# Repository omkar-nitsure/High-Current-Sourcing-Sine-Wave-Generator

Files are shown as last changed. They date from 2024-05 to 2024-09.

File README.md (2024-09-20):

# High Current Sourcing Sine Wave Generator

Group Members -

1. Omkar Nitsure - 210070057
2. Ojas Karanjkar - 210070040
3. Kushal Gajbe - 210070048
4. Vaibhav Garg - 21d070085 <br>
Github Link - [All files and code Contents](https://github.com/omkar-nitsure/High_Current_Sourcing_Sine_Wave_Generator)

## Introduction

Magnetic Materials are used in many application and in many different equipment for their special properties. But before using them, we need to have in-depth knowledge of their characteristics. This requires performing BH characterization. In BH characterization, we need to apply a sinusoidal voltage of varying amplitude and frequency across the magnetic material and check for the current it draws. Then the current and voltage information can be used to compute the value of B and H. The area enclosed by this curve is an indication of the amount of power dissipation in the material. This and other information is vital for choosing the right material for a specific application.

So, now we understand why BH characterization is important. We need a source which is able to generate a sinusoidal voltage with varying amplitude and frequency and source the current drawn by the magnetic material. The aim of our project is to design such a source.

This problem can be tackled either using a digital + analog or only analog approach. We tried both approaches. We designed an analog only circuit comprising of Class-AB amplifier and for the digital + analog we have used a Class-D amplifier based circuit. Let's discuss both the approaches in the following sections -

## Target Specifications

We were required to build a source satisfying the above constraints -

- Output Frequency = 2-3 kHz
- Output Sine amplitude = upto 30 Vpp
- Current Sourcing capacity = 1-1.5 A
- Added functionality of allowing user to change frequency on the go using a knob. - Display the current frequency on a LCD screen for ready reference

## Class Ab Based Circuit

In this approach, we designed a circuit which can be broken down in a Voltage amplification circuit and a Current sourcing circuit and connected them in cascade. The circuit diagram is as follows -

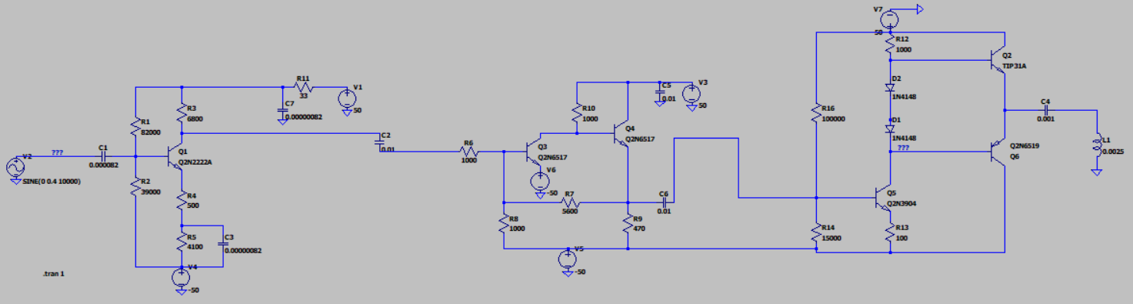
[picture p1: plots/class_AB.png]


Figure 1: Circuit diagram for Class AB amplifier based circuit
The above circuit was giving the correct required output but there was an issue. There was a lot of power dissipation in the different BJTs which would have required big heat sinks and also a lot of power would have got wasted along with the unavoidable power loss due to eddy currents. We tried changing a lot of different parameters but we were not able to reduce the power-loss to the desired levels. While we were searching for the potential solution, we came across class-D amplifier which was not having the issue of power loss. After a lot of brainstorming, we decided to scrap this approach and continue with the approach involving Class-D amplifier.

## Class D Amplifier

Class D amplifier consists of a full-bridge MOSFET based circuit. Each of the 4 MOSFETs are fired by 4 different PWM signals across their gate-source. Two MOSFETs in the same leg get complementary PWM signal such that there ON times are separated by a non-zero dead time.

This dead-time is provided to ensure that there is sufficient time for the MOSFETs to change their states ensuring that both MOSFETs don't turn-on together and short Vdd with GND.

The duty ratio of the PWM signals vary sinusoidally which enables the output to be sinusoidal.

Duty ratios of the 4 PWM signals are as follows -

$$
d_{1} = \frac{1}{2} + m \sin(\omega t)
$$

$$
d_{2} = \frac{1}{2} - m \sin(\omega t)
$$

Then d3 and d4 are just complements of d1, d2 respectively seperated by dead time.

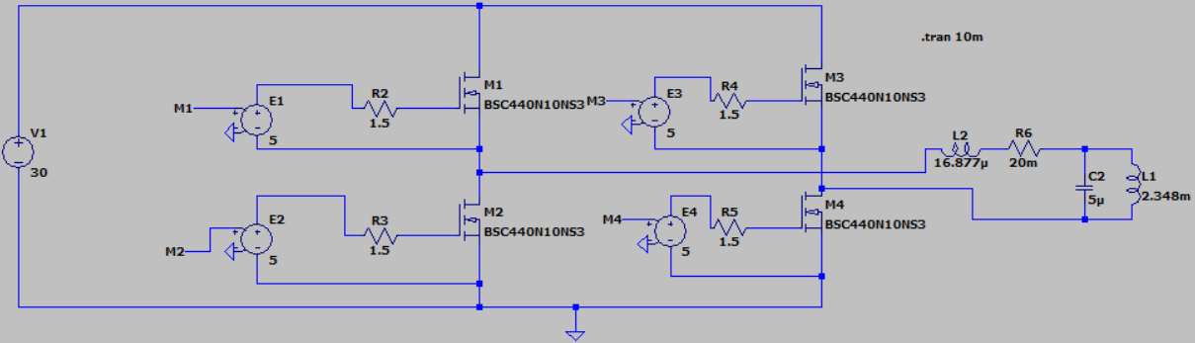
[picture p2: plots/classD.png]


Figure 2: full-bridge MOSFET based circuit

## A. Simulations

We performed the LTSpice simulations of class D amplifier for our required specifications and got desired results. We generated the sinusoidally varying PWM signals by giving a triangular wave and a sine wave as inputs to a comparator. We kept zero dead time assuming perfect switching of MOSFETs. The MOSFETs were switching at a frequency of 100kHz and we tested the sinusoidal outputs for frequencies till 3kHz which was our target specification. We also checked for the power dissipation in the entire circuit(in all components) and found that they were in mW. Thus this approach allowed us to generate sine waves of large amplitudes for frequencies upto 3kHz without requiring any heat-sink at all!! This approach has some cons but that is a trade-off for excellent efficiency. The main limitation of this approach is that it generates saw-tooth noise because of MOSFET switching whereas a purely analog approach will not add any such noise. The results of our simulations are given below where the output voltage across the inductive load is given at the edge of our required specifications. We also give the corresponding current drawn by the inductive load which is well within our specifications.

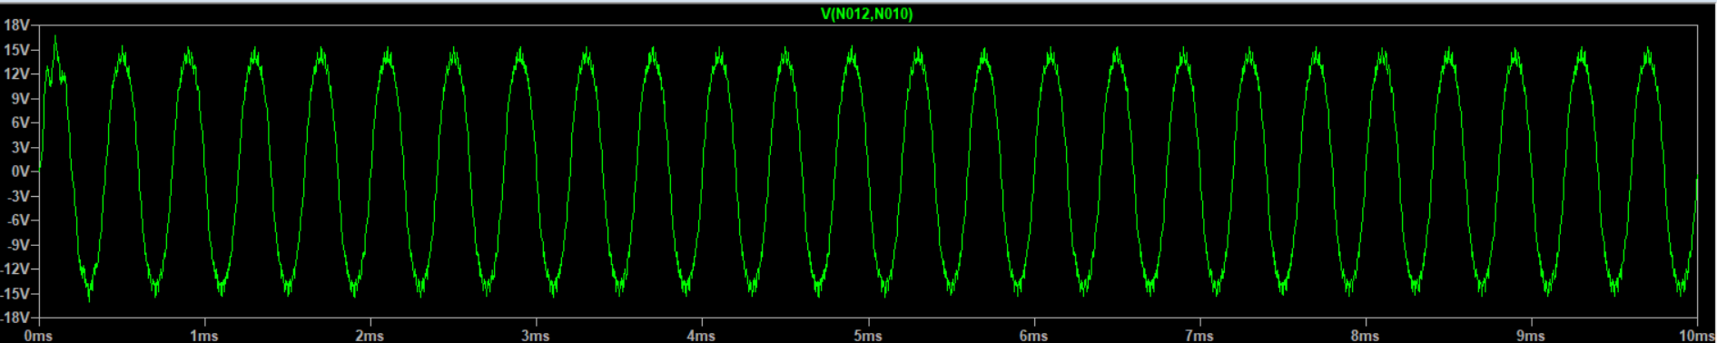
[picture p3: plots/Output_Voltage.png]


Figure 3: output voltage across load

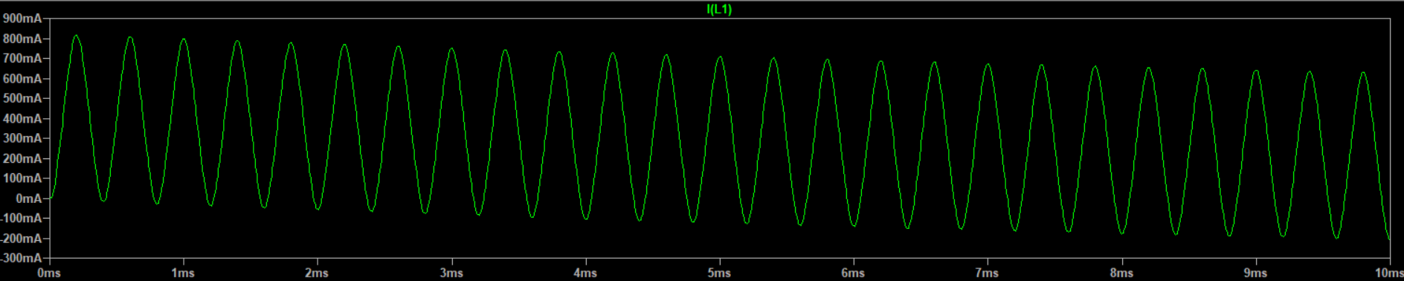
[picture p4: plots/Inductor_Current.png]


Figure 4: Current through the inductive load

## B. Choice Of Bom And Justifications

The Bill of Materials required for our circuit is as follows -

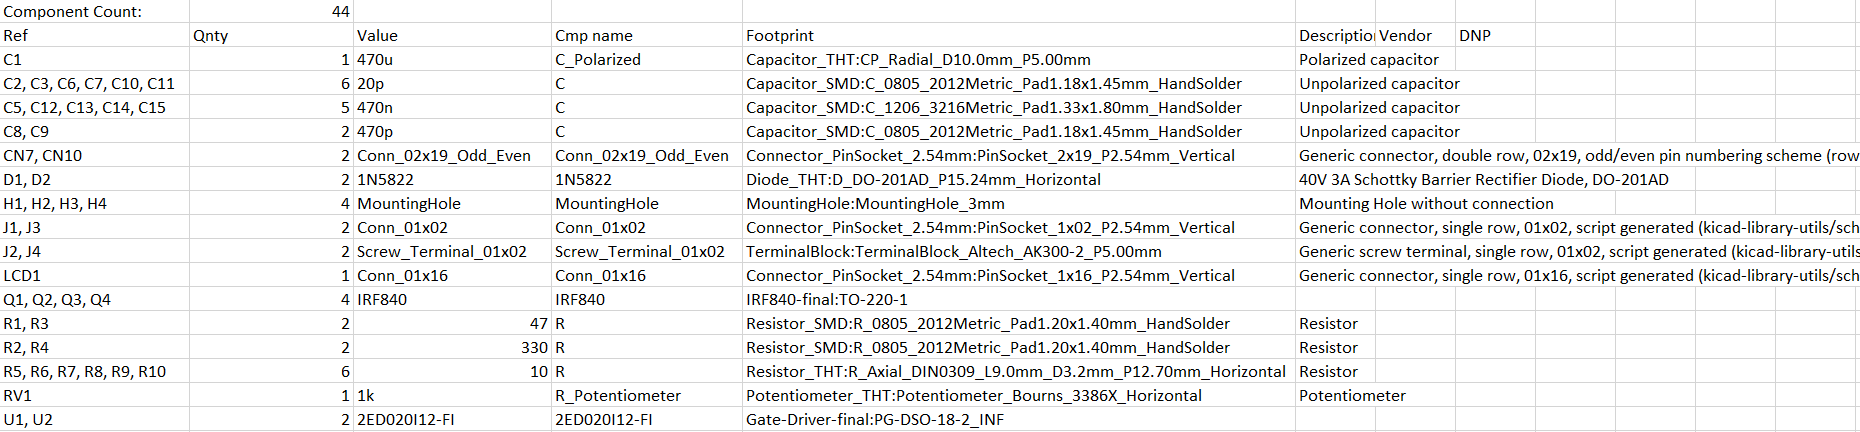
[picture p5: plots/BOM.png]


Figure 5: Bill of Materials

Gate Drivers - The PWM output cannot be directly given to the gates of MOSFETS as the back-currents generated while a MOSFET is turning-OFF will certainly damage the GPIO
pins on the Micro-controller. We wanted to have a gate driver which can amplify the rail-to-rail logic of 3.3 V coming from the micro-controller to rail-to-rail logic of 15V. We also wanted the current sinking capacity to be high which will allow us to switch at much higher frequency. Thus we chose the 2ED02012-FI gate driver from Infenion STM32 minimum package called Bluepill was more than sufficient for our ap-
Bluepill -
plication. It was able to generate the 4 independent PWM signals. It also had ADC which was used to provide the functionality of a knob for changing the output frequency to the user. We also needed 4 additional analog pins to write current frequency value on the LCD display. All of these requirements were satisfied by Bluepill.

RC filter at the input of the gate driver - This low-pass filter was used to remove the high-frequency peaks in the PWM outputs of the microcontroller.

MOSFET - We wanted to produce output sinusoidal signals of 30 Vyp and thus the Vas specifications of the MOSFETs must be larger than this value. We also wanted to source currents upto even 2A and thus the Ids rating must be larger than this value. We also wanted the MOSFET
to be a power MOSFET having the capability of very fast switching. MOSFET named IRF840 satidfied all these constraints and thus we chose that MOSFET for the circuit. LC circuit at the output - We had to use a low-pass filter at the output of a Class-D
amplifier to remove the saw-tooth noise added due to switching. We could have used a RC
filter but that would have resulted in large power-loss in the resistor, so we chose to use LC
filter of appropriate value which would not cause any power-loss.

## Microcontroller Programming

We generate the PWM signal with Sinusoidally varying dead time using the STM32 Bluepill microcontroller. The microcontroller clock frequency is 8MHz. The internal circuitry increases it such that the timers(which we used) get a frequency of 64MHz while the ADC sampling frequency is 8MHz. We decided to keep the switching frequency to be 100kHz which is almost 33 times larger than the maximum rated frequency of our system. It is also well within the maximum attainable switching frequency by the Power MOSFET. We have kept the cut-off frequency to be 12kHz which is less than 10 times the maximum rating. Let us now see how did we generate the PWM signal with sinusoidally varying duty ratio.

## A. Pwm Generation

We used 2 channels from TIM1 on the STM32. Each of these channels have a register named CCR which can be used to manipulate the duty ratio of the microcontroller. So, we stored the values for 1 cycle of the sinusoidal signals corresponding to d1 and d2 in the memory and read those values after a frequency dependent delay. This allowed us to generate sinusoidally varying PWM. Dead-time was also provided to ensure proper switching without any shorting which might damage the MOSFETs. We used a constant dead time of 0.125 us

## B. Adc Interfacing

We wanted to give a simple knob-based control to the user which he can use to set the output frequency he wants. This knob was made using a potentiometer circuit where the ends of the potentiometer are connected to the GND and 3.3V of the microcontroller. The middle pin is connected to the ADC and the values of voltage read using the ADC are then mapped to appropriate frequencies. The ADC is sampled every 1000 cycles to ensure that we don't sample "too often".

## C. Lcd Interfacing

We have also interfaced the LCD with the system so that user can see the current frequency output from the system in real time and adjust the knob accordingly to set the frequency of his choice. We implement the interfacing with 6 pins, 4 of which are the actual data pins. We write the frequency value after every 1000 cycles right after sampling the ADC. Thus we ensure that we don't write to the LCD "too often". The CAD model was then made accordingly to ensure that the LCD is clearly visible to the user.

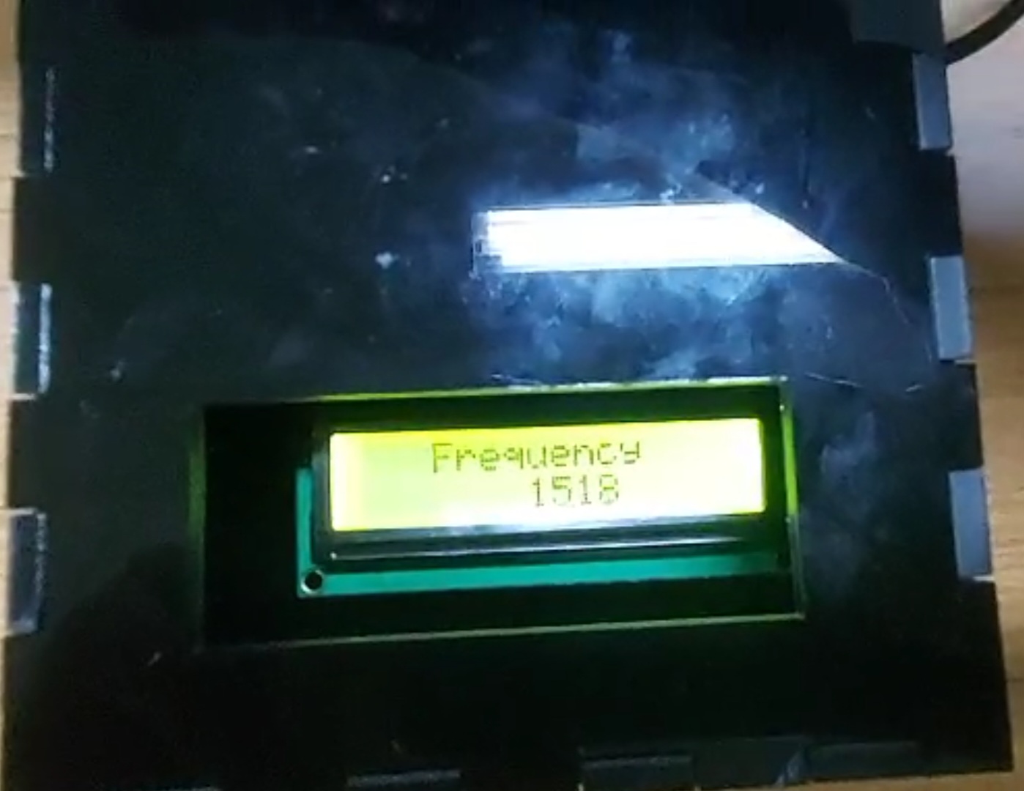
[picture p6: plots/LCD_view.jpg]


Figure 6: LCD in the final prototype

## D. Microcontroller Pinout

The final microcontroller pinout after setting all the GPIO pins and interfacing the ADC and LCD is as follows -
s_JTCK-SW

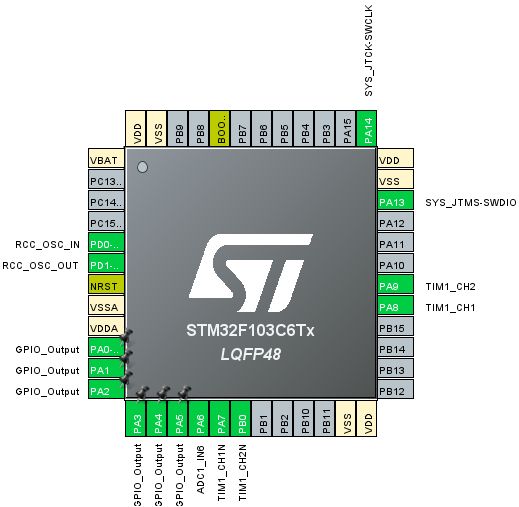
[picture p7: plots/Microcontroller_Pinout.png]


Figure 7: STM32 pinout

## Schematics

Having selected the class D amplifier as the base of our power amplifier, we started making the overall complete circuitry for our prototype. As we have seen so far, our circuit majorly consists of 3 parts, viz

1. Microcontroller - For generating PWM signals.
2. Gate Drivers - For interfacing microcontroller with MOSFETs.
3. Full-bridge MOSFET
In our circuit, we have directly used Blue-Pill, which is a miniature version of NUCLEO-
F103RB STM32 evaluation board. The reason for going with blue-pill is simply because it contains all of the features of NUCLEO board we required and moreover, it is smaller in size.

However, one main issue while using blue-pill is that it does not have emulator part, which is present in NUCLEO board, making it difficult to dump code onto it. We had to use the ST-Link debugger everytime we wanted to dump our code onto blue-pill.

Moving onto the next part of our circuit, we have Gate Drivers. We chose the 2ED020I12-FI
IC manufactured by Infineon. The IC can sustain high voltage up to 1.2kV, supplying currents up to 1A or -2A. The PWM signals generated by the blue-pill were then fed to the gate drivers through the RC filter. This reduces the spike levels due to switching in the microcontroller.

A major part of the gate driver circuitry is the Bootstrap circuit at the high-side output of the gate driver IC. The bootstrap circuitry is used to supply bias to high-side FET. When the low-side FET is ON, the HS pin and source of the high-side FET are pulled to the ground.

As a result, the bootstrap capacitor is charged to Vdd. When the high-side FET is ON in the next cycle, the bootstrap capacitor discharges some of its charge to the gate of FET, thereby creating some positive Vgs and turning on the FET. Schottky diode is used as the bootstrap diode because of its ability to switch at high frequencies. Calculation of bootstrap capacitance is an important step while designing the bootstrap circuit. The value of bootstrap capacitor is calculated according to the given formula -

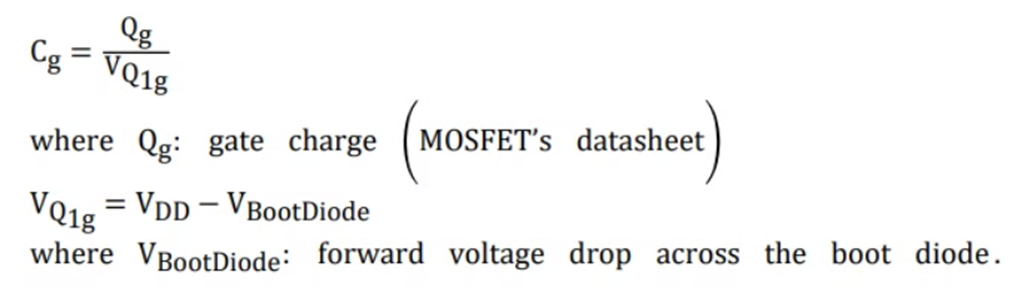
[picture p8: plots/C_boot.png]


Figure 8: Gate Driver Circuit
For IRF540N, the value of gate charge is 66nC, and for 1N5822 Schottky diode, the forward voltage drop is 0.525 V, and Vdd = 15V. Plugging the values in above formula gives, Cg =
4.56 nF The minimum value of bootstrap capacitance should be chosen such that, Cboot =
10xCg Therefore, the value of bootstrap capacitor should be atleast 45nF. Apart from that, we also need to add a bypass capacitor value to Vdd, and the value of bypass capacitor should be atleast 10x the bootstrap capacitance. Therefore, Cbypass should be atleast 450nF.

Now, finally, once we have the pulses at the output of gate drivers, they are passed onto the respective gates of the FETs. The pulses are passed onto the gates of FETs through a resistor.

The output is observed between the source of the two high-side FETs. An electrolytic capacitor is connected between the Vdd and GND and ceramic capacitors need to be connected betweent the drain and ground of each FET. A simple low pass filtering is performed at the output to

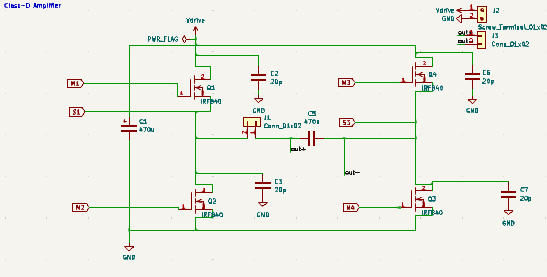
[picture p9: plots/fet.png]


Figure 9: Class-D amplifier
remove spikes due to switching.

We have also added a provision in our circuit to control the frequency using a knob. The knob is connected to a 10kΩ potentiometer. Based on the voltage at the middle terminal of the the voltage is sensed by the ADC in the blue-pill and it is mapped to the corresponding frequency value. The current frequency value is displayed using an LCD. Finally, putting all parts together, we get our final circuit schematics.

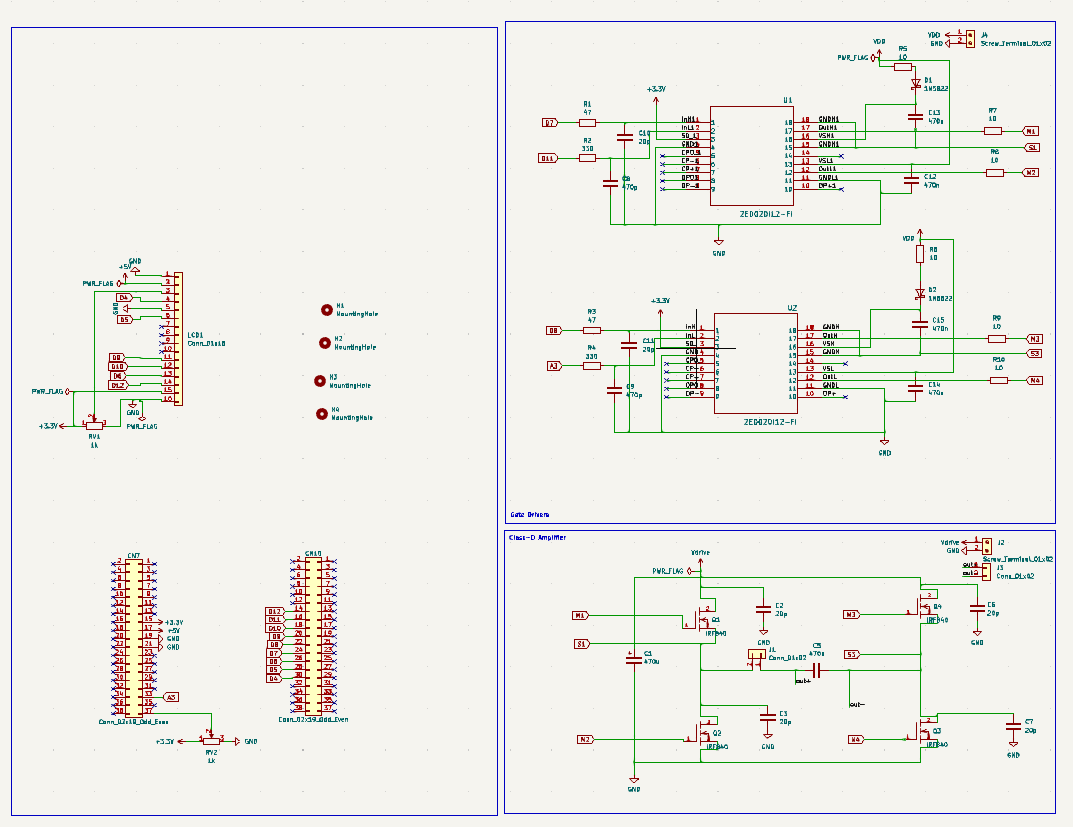
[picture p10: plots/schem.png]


Figure 10: Full circuit schematics

## Intermediate Testing

## A. Pwm Generation

As descibed in 5.1, we generated the PWM signals using STM32 and tested. The output is shown in the image below.
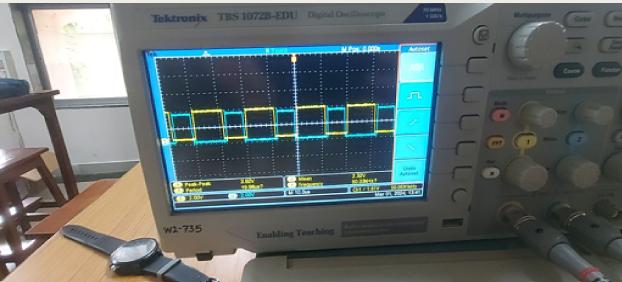
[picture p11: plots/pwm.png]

Figure 11: PWM testing

## B. Adc Interfacing

We were able to interface a potentiometer with the microcontroller using an ADC successfully.

## C. Breadboard Testing

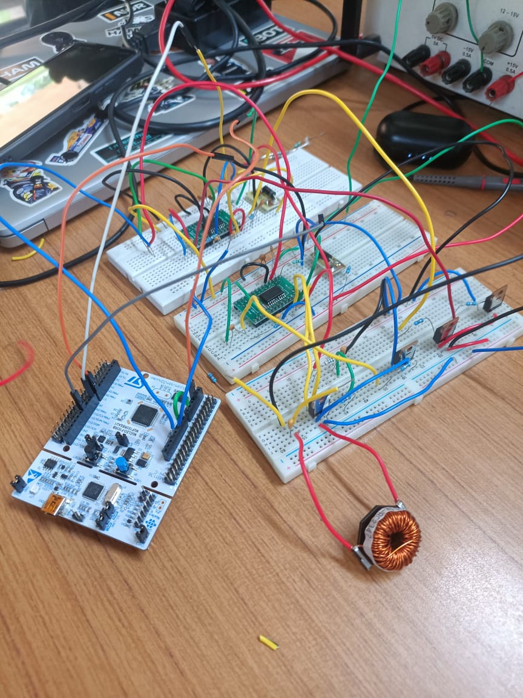
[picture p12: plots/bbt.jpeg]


## Pcb Design

We designed the PCB using the KiCAD software. Various layout rules such as obtuse angles between tracks, decoupling capacitors, and correct placement of components were taken care of. We have used both SMD and THT components in our design. We have majorly used SM
components for decoupling capacitors and the gate driver IC. We have used screw terminals for connecting the inputs to the PCB. The blue pill is mounted on the PCB using a breakout board.

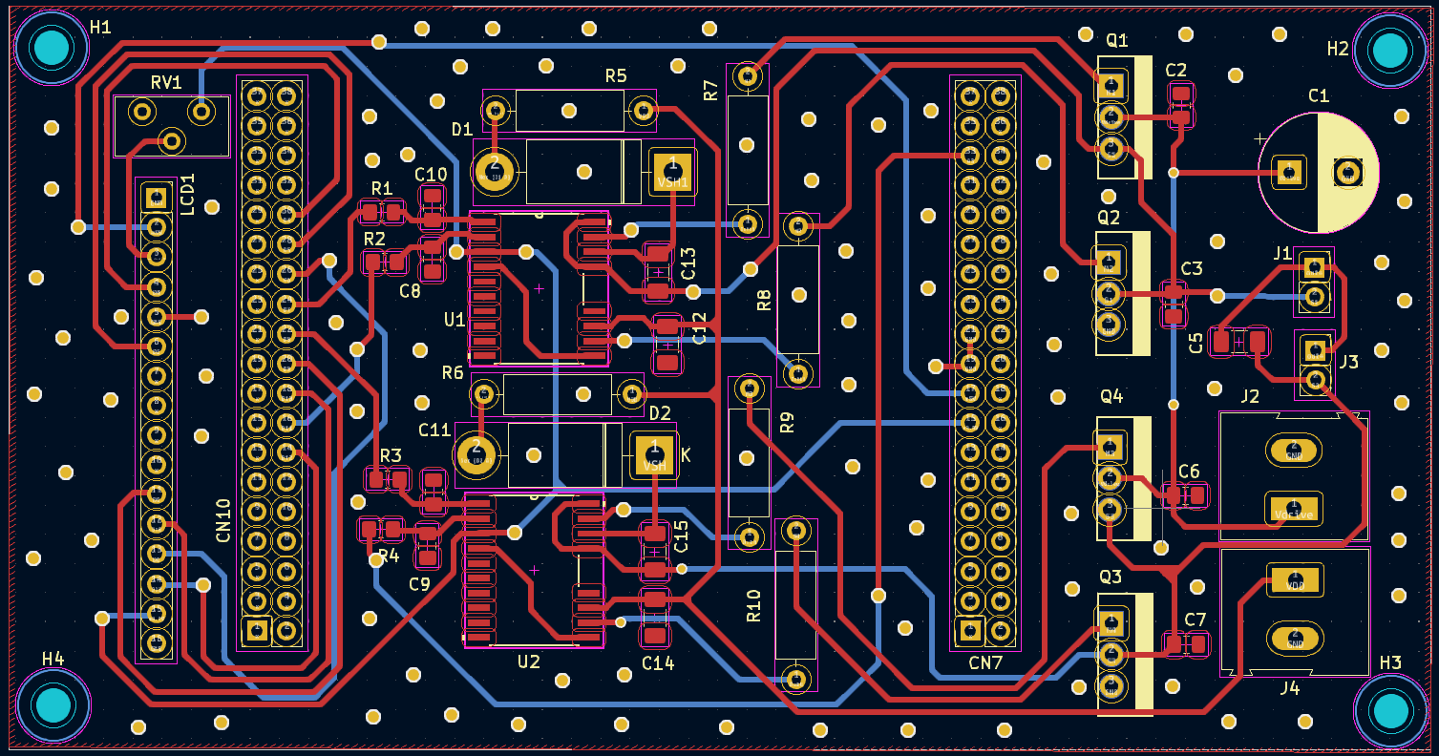
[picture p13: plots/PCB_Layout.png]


Figure 12: PCB Layout

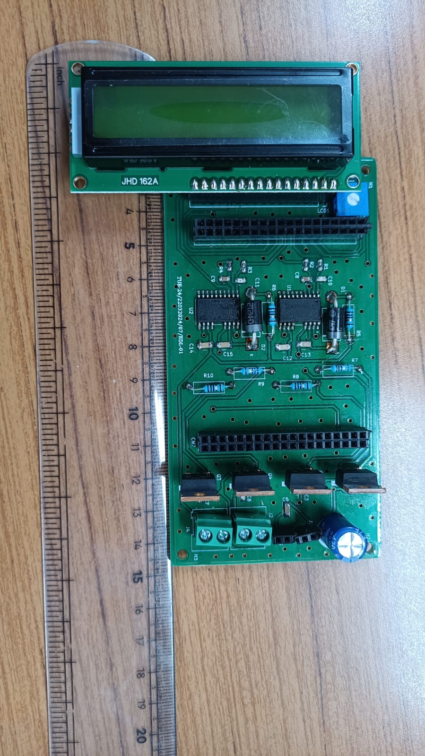
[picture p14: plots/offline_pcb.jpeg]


Figure 13: PCB with all components

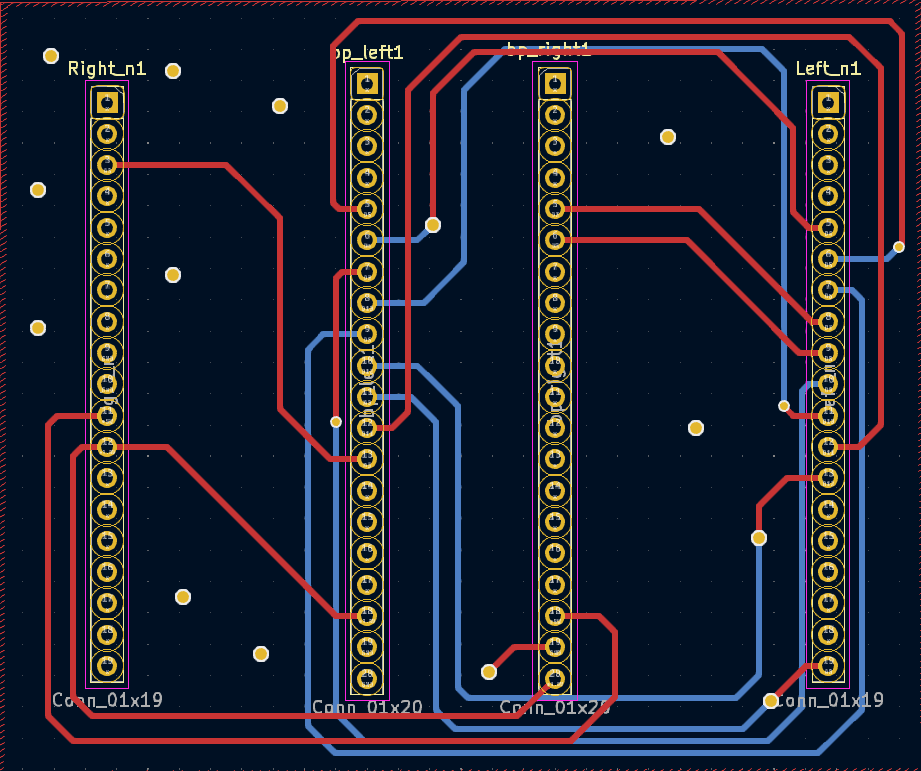
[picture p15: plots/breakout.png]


Figure 14: PCB for breakout board

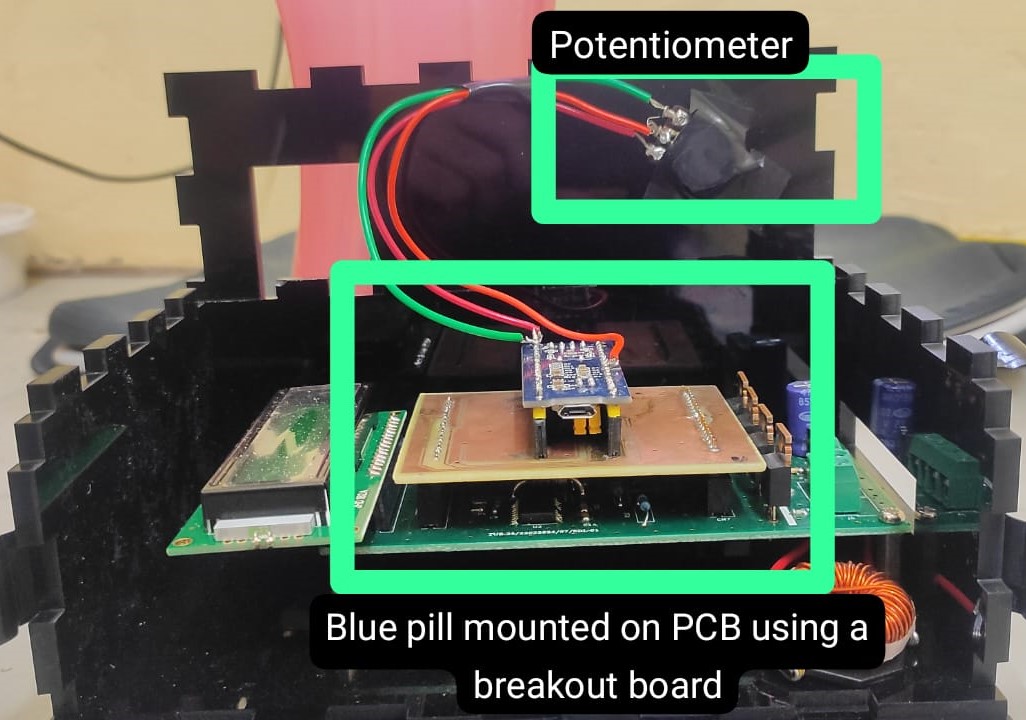
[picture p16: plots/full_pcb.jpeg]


Figure 15: Final PCB

## Cad Design

For our CAD design, we initially planned a 3D box structure using Fusion 360 software. The design process involved careful planning to ensure accessibility to certain components from the outside world while the prototype remains inside the box.

## A. Design Requirements

1. LCD Display: The design incorporates an open area for the LCD display to allow users to observe the frequency without obstruction.

2. Input and Outputs:

- Power Supply: A 5V supply is provided through a USB cable, which is also utilized for burning code onto the STM32 microcontroller.
- External Supplies: Vdrive and Vdd are supplied externally.
- Output Access: The output across the capacitor is also accessible through an opening on the 3D box.
- Potentiometer: A potentiometer is mounted on the box which will be used for controlling the frequency of the prototype. Thus, certain areas must be opened up on the box for the same.

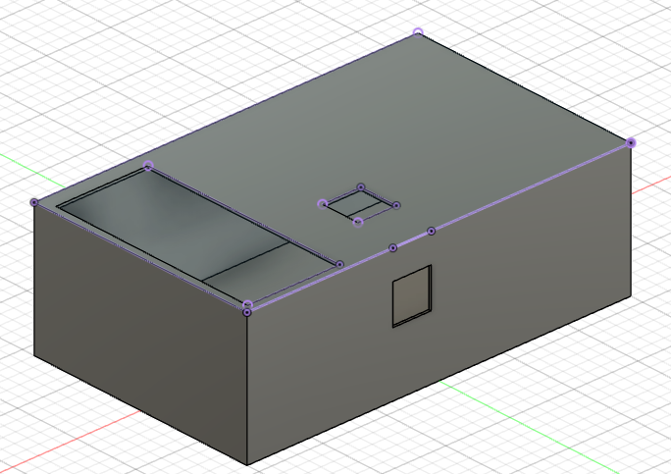
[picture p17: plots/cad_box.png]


Figure 16: 3D box CAD design
However, after discussing the design with the faculty we concluded that 3D printing the box is not possible, and hence we would have to use acrylic sheets laser cutting to make our box.

Now, makercase was used for making the dxf file which has the thickness of the sheet, length, and width for each side of the box. After importing this dxf file into the Fusion 360 software, we cut out the same regions as in the 3D box design.

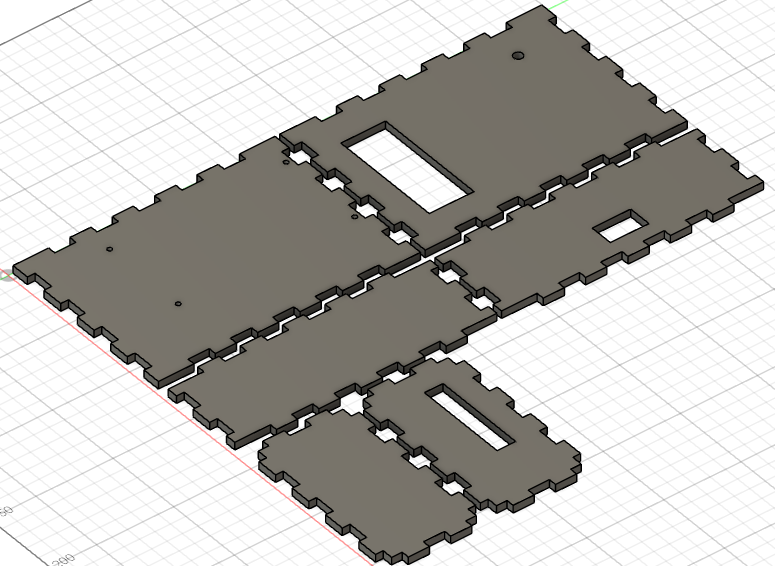
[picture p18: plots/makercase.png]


Figure 17: Acrylic sheets design for the box

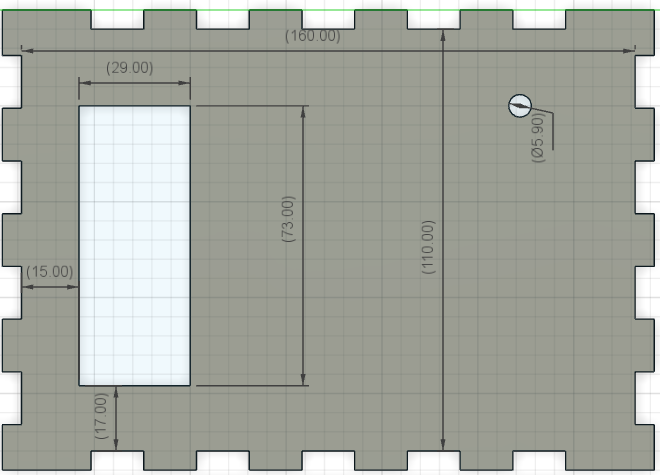
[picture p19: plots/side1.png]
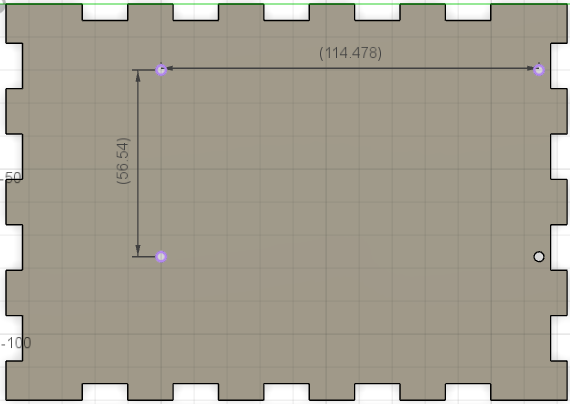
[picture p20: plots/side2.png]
|  |  |
| ----------------------------------- | ----------------------------------- |
| (a) Top side                        | (b) Bottom side                     |

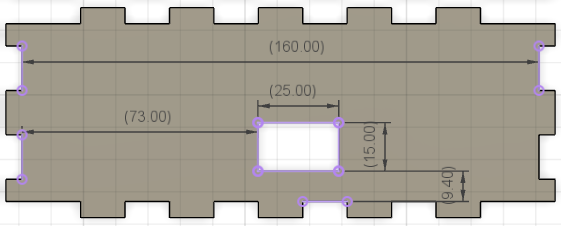
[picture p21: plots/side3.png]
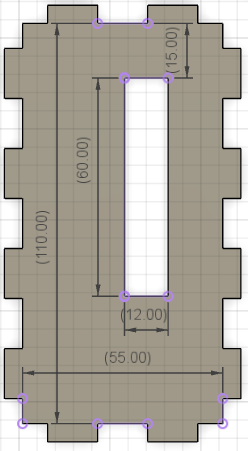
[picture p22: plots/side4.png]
|  |  |
| ----------------------------------- | ----------------------------------- |
| (c) Front view side                 | (d) Side view                       |

Figure 18: Dimensions and open areas in the design.

## Final Prototype

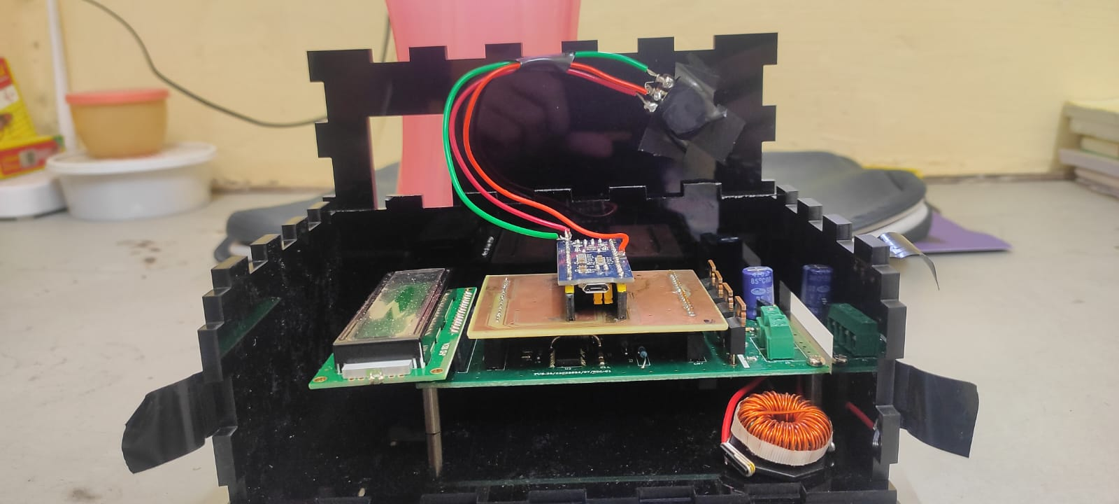
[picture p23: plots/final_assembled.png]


Figure 19: Final Prototype

## Results

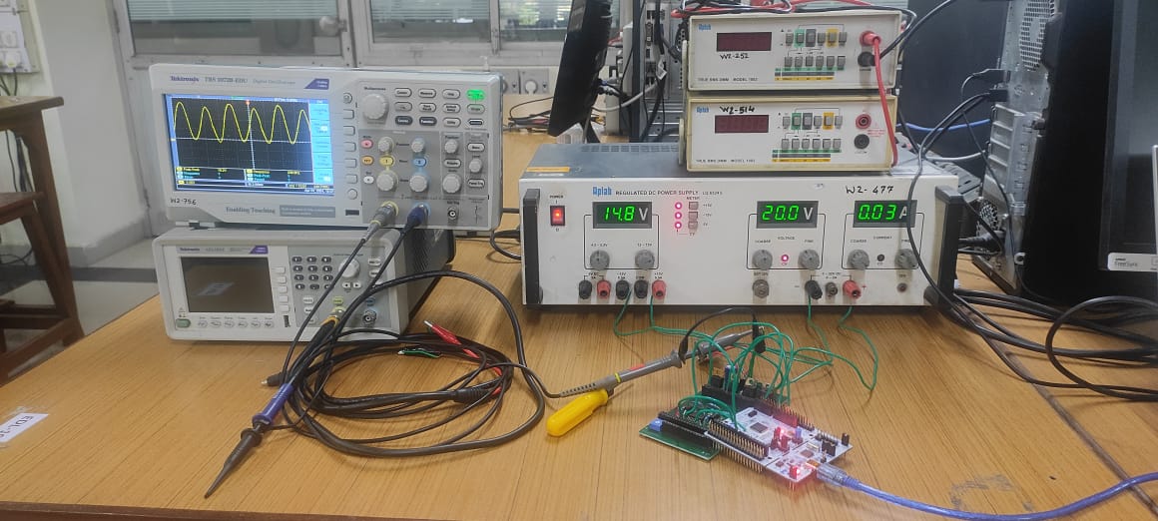
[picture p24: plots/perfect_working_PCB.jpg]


Figure 20: Final output Sine waveform
Our final output waveform is a sine wave meticulously designed for the characterization of magnetic materials. The waveform is derived from three power sources: Vdrive, Vdd, and a 5V supply via USB to the Nucleo board. The output signal is measured across a 470nF capacitor. Our setup achieves a current rating of 1.4 A, with the peak-to-peak voltage (Vpp) reaching up to 30 V at a frequency of 500Hz.

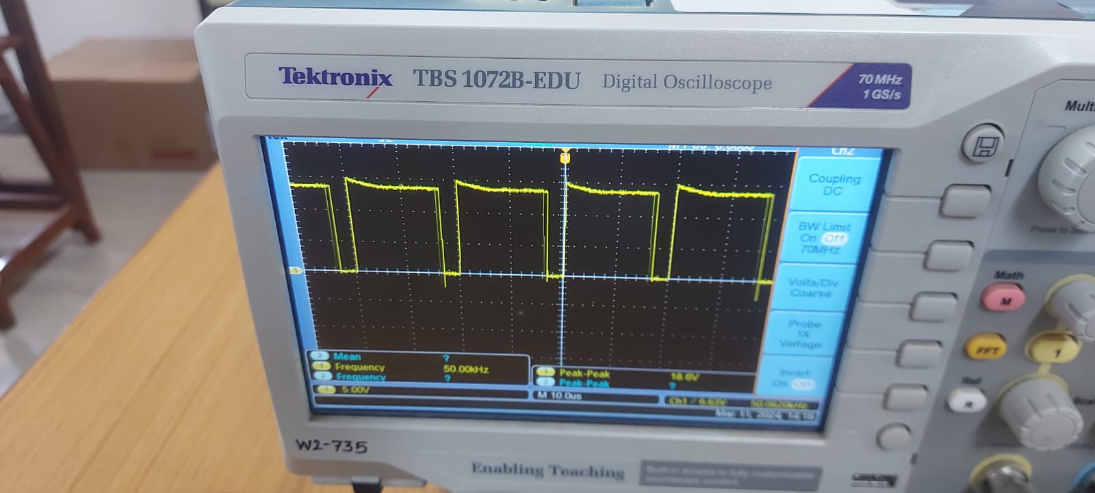
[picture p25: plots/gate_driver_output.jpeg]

Figure 21: Gate Driver output

The output from the gate driver pertains to the high side. As anticipated, it effectively amplifies the PWM signal from the microcontroller. We are able to achieve 18.6 V of peak-topeak voltage output from the gate driver.

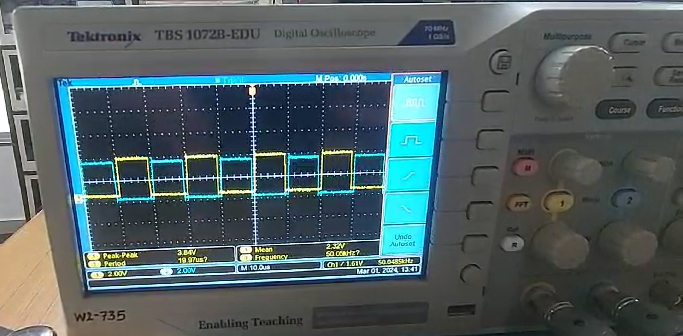
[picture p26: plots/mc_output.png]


Figure 22: Microcontroller output. 
Above is the microcontroller PWM output. This goes as an input to our gate drivers. This PWM peak-to-peak voltage is 3.84 V. This is then amplified to 18.6 V by the gate drivers.

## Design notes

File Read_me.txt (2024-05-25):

                                       READ ME FILE
---------------------------------------------------------------------------------------------
----------------------------------------------------------------------------------------------

1. CAD - Design files for the project used in Autodesk Fusion 360.

2. datasheets:- Datasheet of important components used in our circuit design

3. Images:- All outputs and PCB images of the project

4. LTSpice_Simulations:- LTSpice files for our final circuit. Simulation images are included inside.

5. Papers:- All the research papers which we had referred to for our project. 

6. PCB_Files:- PCB files generated for our circuit design in the KiCAD software. 

7. Report:- Final report of our project. It has everything we have done in our project. 

8. STM32_Bluepill_code:- Main code which was used for making PWM and LCD interfacing. Programming done in CUBEIDE.

9. project_plan.pdf:- It has our decision making and the plan for our project which we had followed. 

10. USER-Manual:- User manual for using the prototype. 

---------------------------------------------------------------------------------------------
---------------------------------------------------------------------------------------------

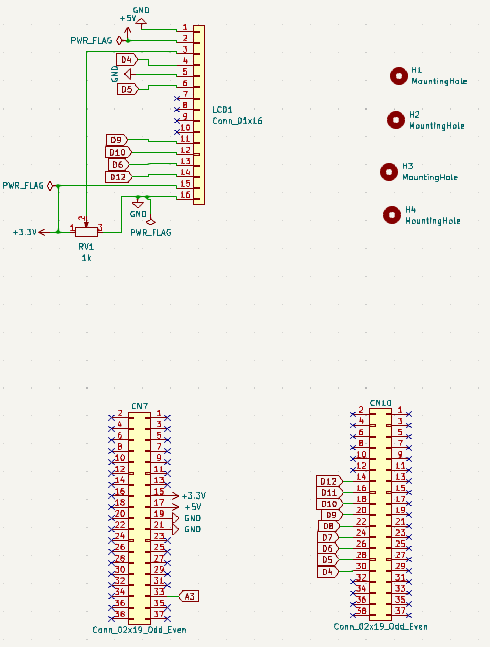
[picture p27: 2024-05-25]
Images/LCD_Microcontroller_Schematic.png

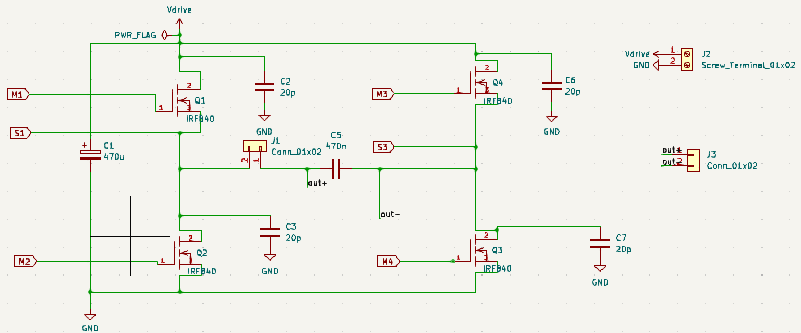
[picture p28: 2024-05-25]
Images/ClassD_Amplifier_Schematic.png

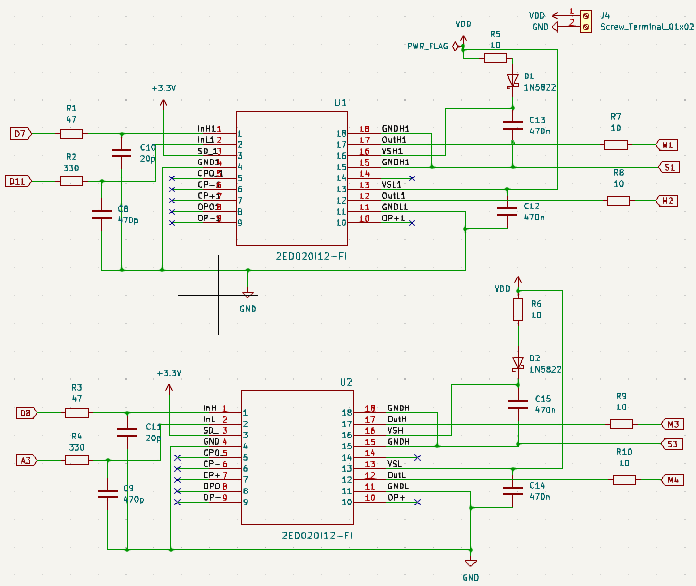
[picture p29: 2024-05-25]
Images/Gate_Driver_Schematic.png

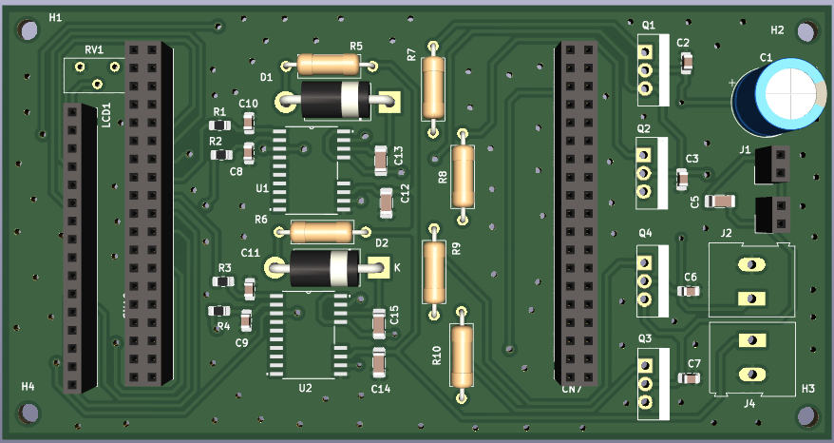
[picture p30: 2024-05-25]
Images/PCB_3DViewer.png

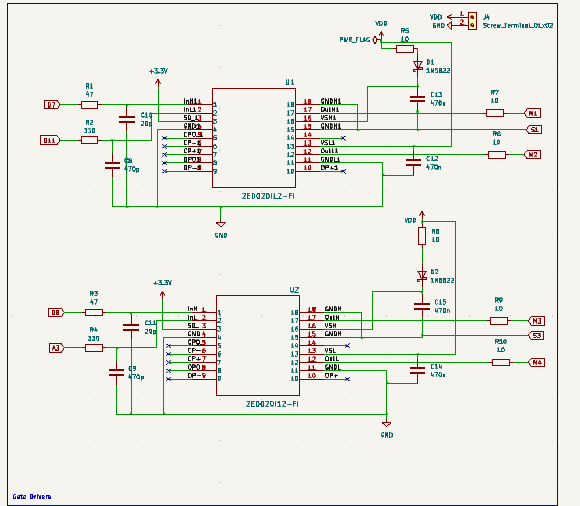
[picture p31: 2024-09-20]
plots/gate_drivers.png

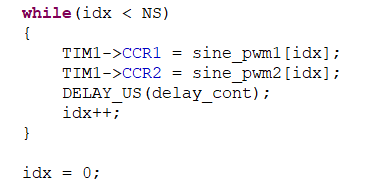
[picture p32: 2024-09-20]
plots/PWM_snippet.png

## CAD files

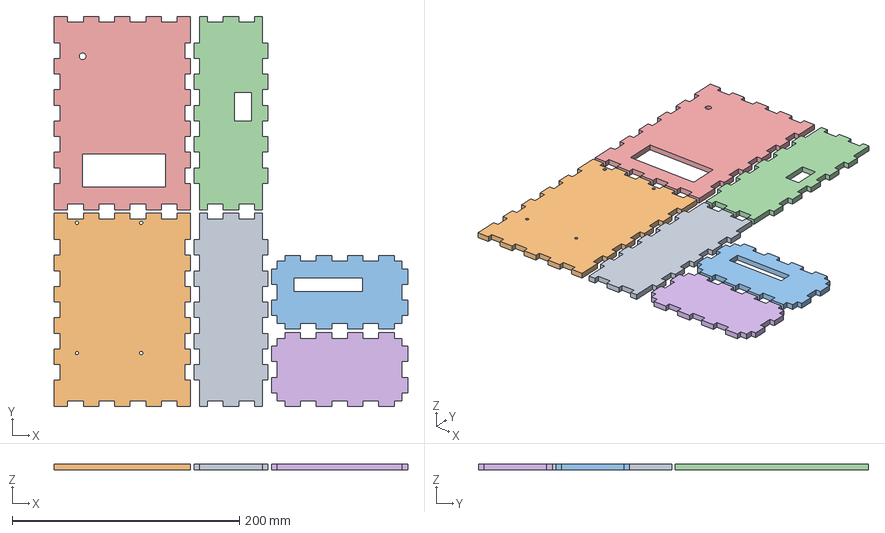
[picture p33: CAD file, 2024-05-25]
CAD/box_box_ii v2.3mf
311.0 x 343.0 x 5.00 mm

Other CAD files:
CAD/box_box_ii v2.dxf
CAD/box_box_ii v2.f3d
CAD/box_box_ii v2.ipt

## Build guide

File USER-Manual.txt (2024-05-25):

                      USER MANUAL         
--------------------------------------------------------------------------

1. There are three inputs to the prototype. 
	i. Vdd :- takes value of 15V 
	ii. Vdrive (or Vin) :- 0-30V
	iii. USB :- gives 5V supply and can also be used for dumping a different code on the Bluepill.

2. There is a rotary knob for potentiometer. This is used to vary the frequency of the final output sinusoidal waveform. 

3. Vpp for output sine wave can be varied by changing Vdrive. 

4. LCD display is used for displaying the output sine wave frequency. It varries by a few Hz from the actual frequency. 

5. Inductor load is connected on external breadboard. Range:- 1 to 10 mH. 

6. Series resistor load with the inductor is also connected on external breadboard. Range:- 0 to 10 ohms. 

7. Frequency display range:- upto 3kHz. 

8. Current across resistive load - for R = 1.2 Ohm and L = 1mH we get current upto 3.16 A

9. Output is taken from female header output pin which is not adjacent to the electrolytic capacitor, i.e leave the pair of pins adjacent to the electrolytic capacitor and take output from the next pair of pins. 

System should be able to drive currents lower than this value

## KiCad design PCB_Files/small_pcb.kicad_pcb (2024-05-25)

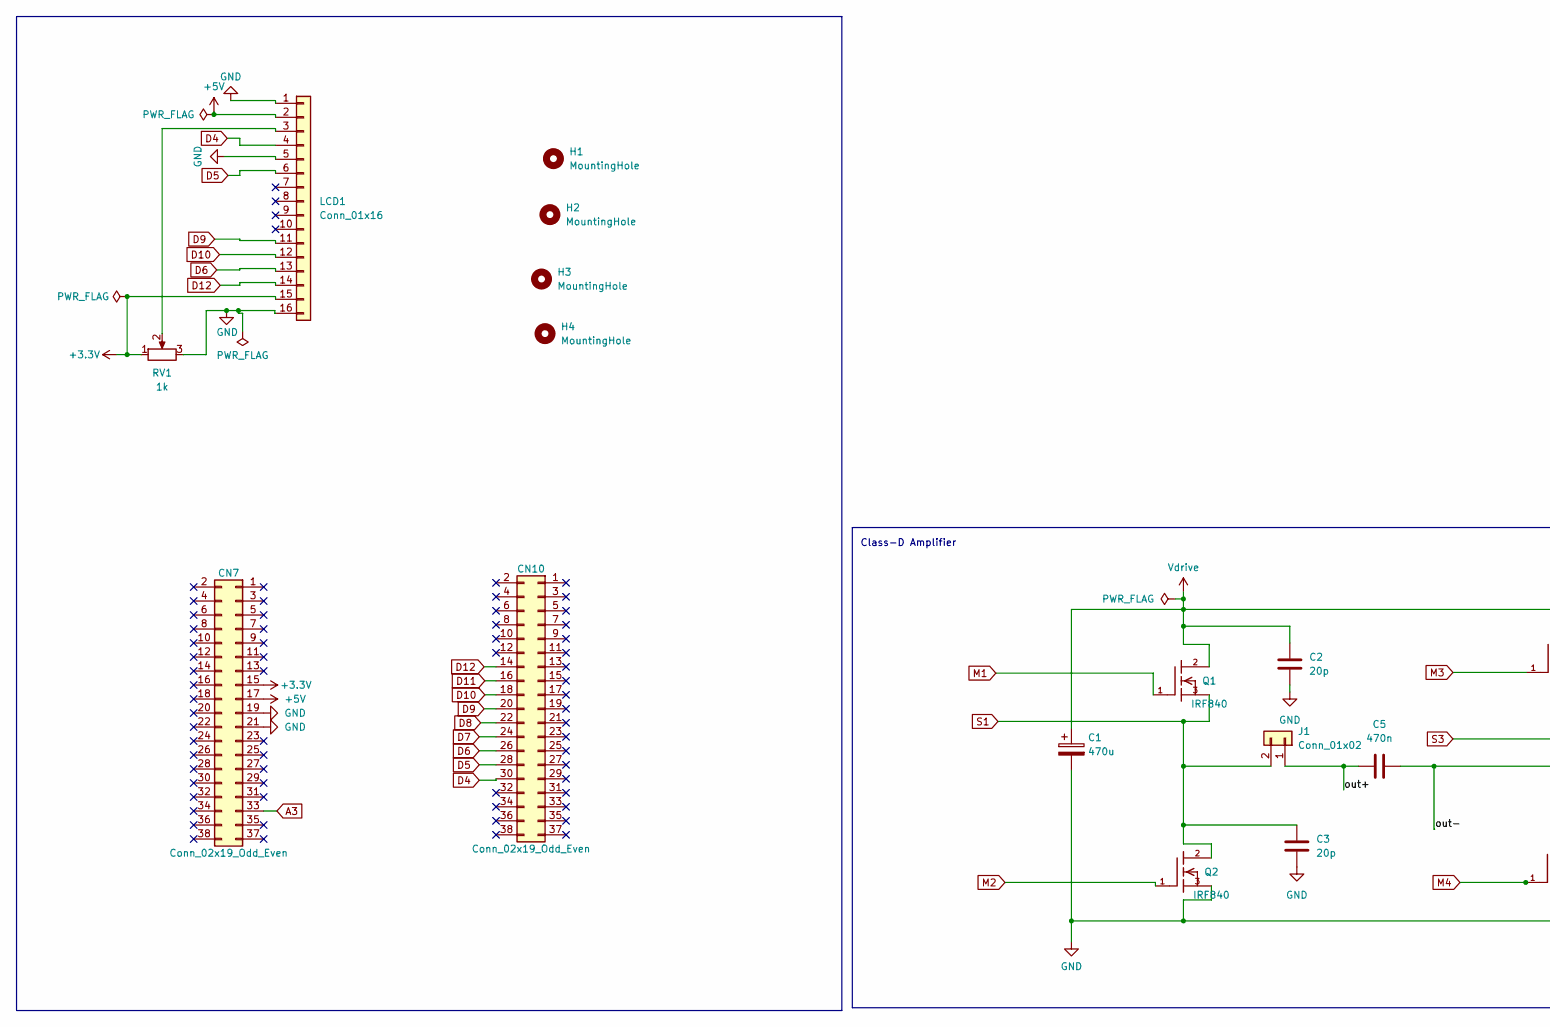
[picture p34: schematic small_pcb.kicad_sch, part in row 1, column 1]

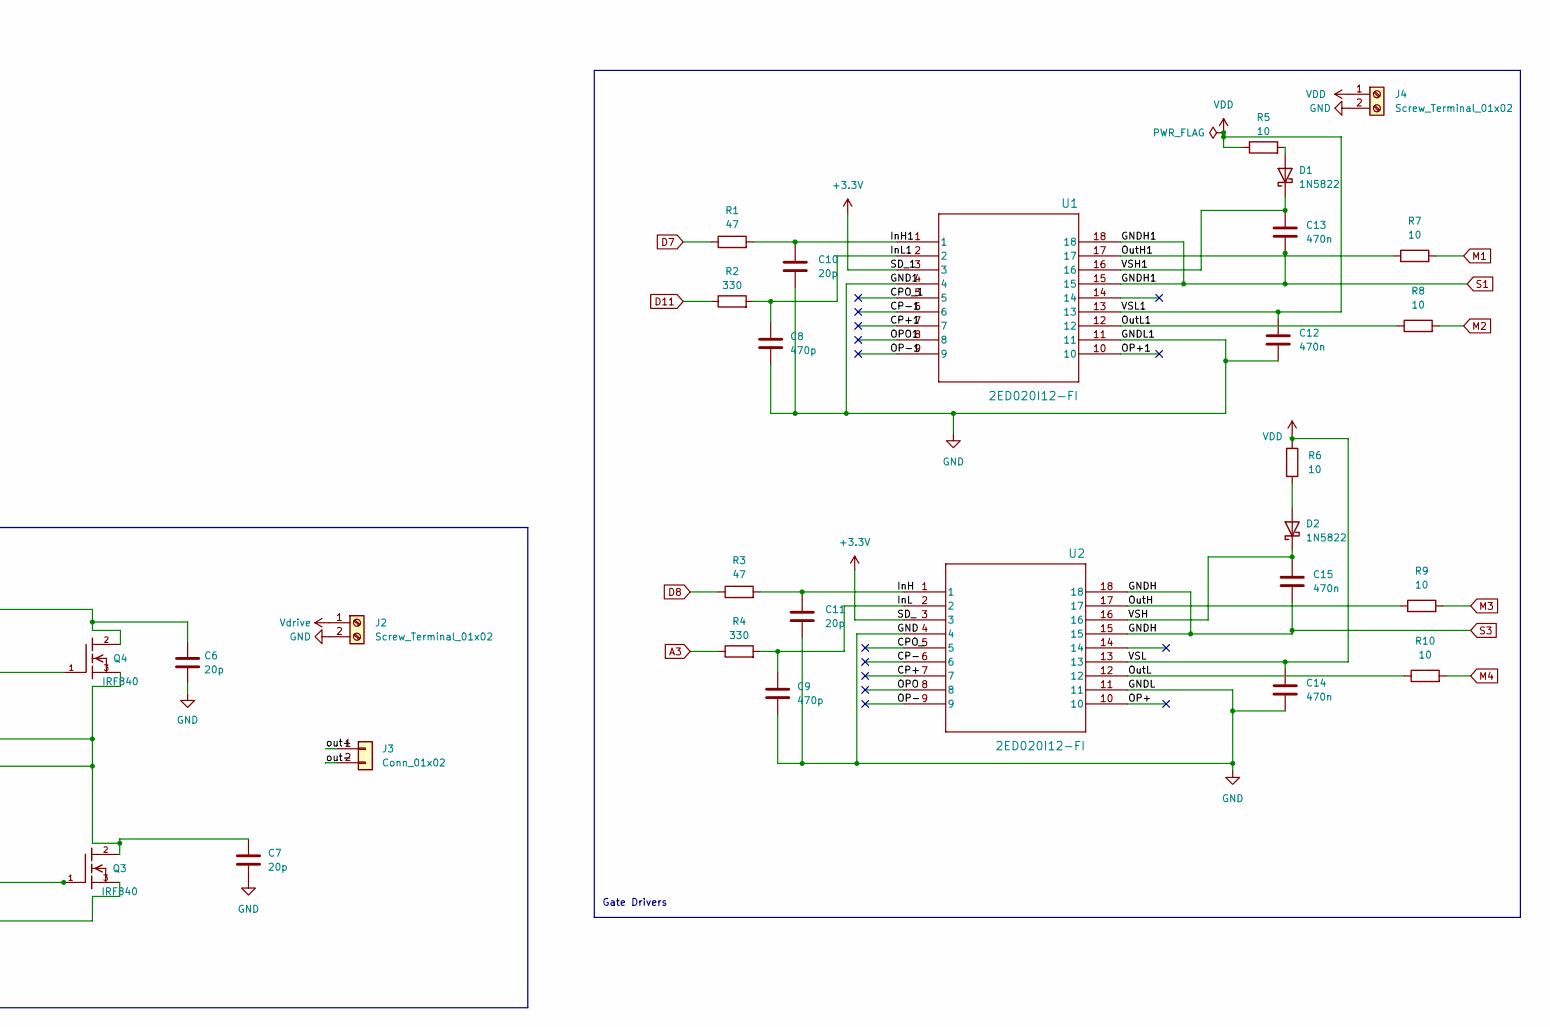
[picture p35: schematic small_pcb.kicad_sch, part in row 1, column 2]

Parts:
C1: 470u; CP_Radial_D10.0mm_P5.00mm
C2, C3, C6, C7, C10, C11: 20p; C_0805_2012Metric_Pad1.18x1.45mm_HandSolder
C5, C12, C13, C14, C15: 470n; C_1206_3216Metric_Pad1.33x1.80mm_HandSolder
C8, C9: 470p; C_0805_2012Metric_Pad1.18x1.45mm_HandSolder
CN7, CN10: Conn_02x19_Odd_Even; PinSocket_2x19_P2.54mm_Vertical
D1, D2: 1N5822; D_DO-201AD_P15.24mm_Horizontal
H1, H2, H3, H4: MountingHole; MountingHole_3mm
J1, J3: Conn_01x02; PinSocket_1x02_P2.54mm_Vertical
J2, J4: Screw_Terminal_01x02; TerminalBlock_Altech_AK300-2_P5.00mm
LCD1: Conn_01x16; PinSocket_1x16_P2.54mm_Vertical
Q1, Q2, Q3, Q4: IRF840; TO-220-1
R1, R3: 47; R_0805_2012Metric_Pad1.20x1.40mm_HandSolder
R2, R4: 330; R_0805_2012Metric_Pad1.20x1.40mm_HandSolder
R5, R6, R7, R8, R9, R10: 10; R_Axial_DIN0309_L9.0mm_D3.2mm_P12.70mm_Horizontal
RV1: 1k; Potentiometer_Bourns_3386X_Horizontal
U1, U2: 2ED020I12-FI; PG-DSO-18-2_INF

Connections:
+3.3V: CN7.15, LCD1.15, RV1.1, U1.3, U2.3
+5V: CN7.17, LCD1.2
/CP+: U2.7
/CP+1: U1.7
/CP-: U2.6
/CP-1: U1.6
/CPO_: U2.5
/CPO_1: U1.5
/InH: C11.1, R3.2, U2.1
/InH1: C10.1, R1.2, U1.1
/InL: C9.1, R4.2, U2.2
/InL1: C8.1, R2.2, U1.2
/OP+: U2.10
/OP+1: U1.10
/OP-: U2.9
/OP-1: U1.9
/OPO: U2.8
/OPO1: U1.8
/OutH: R9.1, U2.17
/OutH1: R7.1, U1.17
/OutL: R10.1, U2.12
/OutL1: R8.1, U1.12
/VSH: C15.1, D2.1 (K), U2.16
/VSH1: C13.1, D1.1 (K), U1.16
/out+: C5.1, J1.1, J3.1
A3: CN7.33, R4.1
D4: CN10.30, LCD1.4
D5: CN10.28, LCD1.6
D6: CN10.26, LCD1.13
D7: CN10.24, R1.1
D8: CN10.22, R3.1
D9: CN10.20, LCD1.11
D10: CN10.18, LCD1.12
D11: CN10.16, R2.1
D12: CN10.14, LCD1.14
GND: C1.2, C2.2, C3.2, C6.2, C7.2, C8.2, C9.2, C10.2, C11.2, C12.2, C14.2, CN7.19, CN7.21, J2.2, J4.2, LCD1.1, LCD1.5, LCD1.16, Q2.3, Q3.3, RV1.3, U1.4, U1.11, U2.4, U2.11
M1: Q1.1, R7.2
M2: Q2.1, R8.2
M3: Q4.1, R9.2
M4: Q3.1, R10.2
unnamed: D1.2 (A), R5.2
unnamed: D2.2 (A), R6.2
unnamed: LCD1.3, RV1.2
S1: C3.1, C13.2, J1.2, Q1.3, Q2.2, U1.15, U1.18
S3: C5.2, C7.1, C15.2, J3.2, Q3.2, Q4.3, U2.15, U2.18
VDD: C12.1, C14.1, J4.1, R5.1, R6.1, U1.13, U2.13
Vdrive: C1.1, C2.1, C6.1, J2.1, Q1.2, Q4.2

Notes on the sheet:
Class-D Amplifier
Gate Drivers

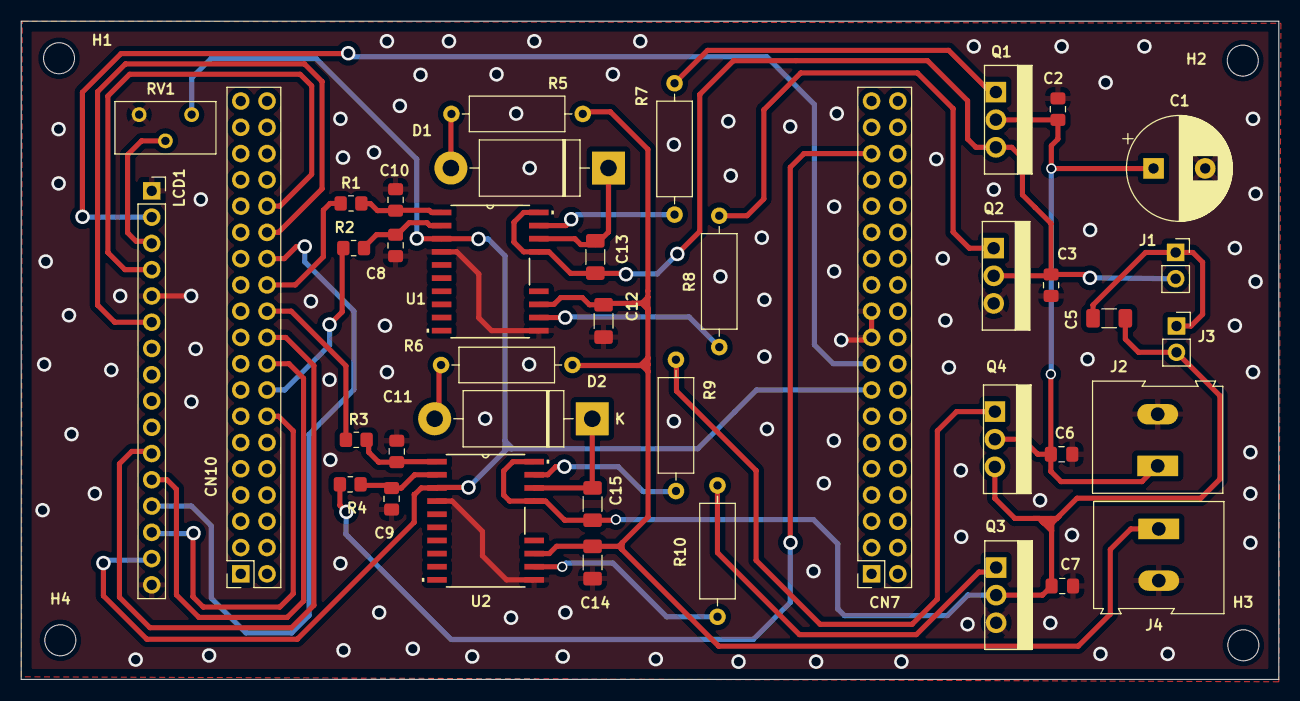
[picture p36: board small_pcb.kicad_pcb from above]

Board: 2 copper layers, 121.6 x 63.7 mm, 44 parts (0 on the bottom side), 35 nets.

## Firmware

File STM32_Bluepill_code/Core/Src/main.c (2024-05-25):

/* USER CODE BEGIN Header */
/**
  ******************************************************************************
  * @file           : main.c
  * @brief          : Main program body
  ******************************************************************************
  * @attention
  *
  * Copyright (c) 2024 STMicroelectronics.
  * All rights reserved.
  *
  * This software is licensed under terms that can be found in the LICENSE file
  * in the root directory of this software component.
  * If no LICENSE file comes with this software, it is provided AS-IS.
  *
  ******************************************************************************
  */
/* USER CODE END Header */
/* Includes ------------------------------------------------------------------*/
#include "main.h"
#include "lcd.h"

/* Private includes ----------------------------------------------------------*/
/* USER CODE BEGIN Includes */
#define NS	100

#define SYSTICK_LOAD (SystemCoreClock/1000000U)
#define SYSTICK_DELAY_CALIB (SYSTICK_LOAD >> 1)

#define DELAY_US(us) \
    do { \
         uint32_t start = SysTick->VAL; \
         uint32_t ticks = (us * SYSTICK_LOAD)-SYSTICK_DELAY_CALIB;  \
         while((start - SysTick->VAL) < ticks); \
    } while (0)
/* USER CODE END Includes */

/* Private typedef -----------------------------------------------------------*/
/* USER CODE BEGIN PTD */
uint32_t idx = 0;

uint32_t pot_value;
uint32_t delay_cont = 20;

volatile uint32_t freq = 500;

const uint32_t sine_pwm1[NS] = {
	460, 469, 478, 486, 495, 503, 512, 520, 527, 535, 542, 549, 556, 562, 568, 573, 578, 583, 587, 590,
	593, 596, 598, 599, 600, 600, 600, 599, 598, 596, 593, 590, 587, 583, 578, 573, 568, 562, 556, 549,
	542, 535, 527, 520, 512, 503, 495, 486, 478, 469, 460, 451, 442, 434, 425, 417, 408, 400, 393, 385,
	378, 371, 364, 358, 352, 347, 342, 337, 333, 330, 327, 324, 322, 321, 320, 320, 320, 321, 322, 324,
	327, 330, 333, 337, 342, 347, 352, 358, 364, 371, 378, 385, 393, 400, 408, 417, 425, 434, 442, 451
};

const uint32_t sine_pwm2[NS] = {
	180, 171, 162, 154, 145, 137, 128, 120, 113, 105, 98, 91, 84, 78, 72, 67, 62, 57, 53, 50, 47, 44, 42,
	41, 40, 40, 40, 41, 42, 44, 47, 50, 53, 57, 62, 67, 72, 78, 84, 91, 98, 105, 113, 120, 128, 137, 145,
	154, 162, 171, 180, 189, 198, 206, 215, 223, 232, 240, 247, 255, 262, 269, 276, 282, 288, 293, 298,
	303, 307, 310, 313, 316, 318, 319, 320, 320, 320, 319, 318, 316, 313, 310, 307, 303, 298, 293, 288,
	282, 276, 269, 262, 255, 247, 240, 232, 223, 215, 206, 198, 189
};

uint32_t iters = 0;
/* USER CODE END PTD */

/* Private define ------------------------------------------------------------*/
/* USER CODE BEGIN PD */

/* USER CODE END PD */

/* Private macro -------------------------------------------------------------*/
/* USER CODE BEGIN PM */

/* USER CODE END PM */

/* Private variables ---------------------------------------------------------*/
ADC_HandleTypeDef hadc1;

TIM_HandleTypeDef htim1;

/* USER CODE BEGIN PV */

/* USER CODE END PV */

/* Private function prototypes -----------------------------------------------*/
void SystemClock_Config(void);
static void MX_GPIO_Init(void);
static void MX_TIM1_Init(void);
static void MX_ADC1_Init(void);
/* USER CODE BEGIN PFP */

/* USER CODE END PFP */

/* Private user code ---------------------------------------------------------*/
/* USER CODE BEGIN 0 */

/* USER CODE END 0 */

/**
  * @brief  The application entry point.
  * @retval int
  */
int main(void)
{
	/* USER CODE BEGIN 1 */

	/* USER CODE END 1 */

	/* MCU Configuration--------------------------------------------------------*/

	/* Reset of all peripherals, Initializes the Flash interface and the Systick. */
	HAL_Init();

	/* USER CODE BEGIN Init */

	/* USER CODE END Init */

	/* Configure the system clock */
	SystemClock_Config();

	/* USER CODE BEGIN SysInit */

	/* USER CODE END SysInit */

	/* Initialize all configured peripherals */
	MX_GPIO_Init();
	MX_TIM1_Init();
	MX_ADC1_Init();
	/* USER CODE BEGIN 2 */
	HAL_ADC_Start(&hadc1);
	TIM1->CCR1 = 451;
	HAL_TIM_PWM_Start(&htim1, TIM_CHANNEL_1);
	HAL_TIMEx_PWMN_Start(&htim1, TIM_CHANNEL_1);

	TIM1->CCR2 = 189;
	HAL_TIM_PWM_Start(&htim1, TIM_CHANNEL_2);
	HAL_TIMEx_PWMN_Start(&htim1, TIM_CHANNEL_2);
	//  /* USER CODE BEGIN 2 */
	Lcd_PortType ports[] = {GPIOA, GPIOA, GPIOA, GPIOA};
	Lcd_PinType pins[] = {GPIO_PIN_2, GPIO_PIN_3, GPIO_PIN_4, GPIO_PIN_5};
	Lcd_HandleTypeDef lcd;
	lcd = Lcd_create(ports, pins, GPIOA, GPIO_PIN_1, GPIOA, GPIO_PIN_0, LCD_4_BIT_MODE);
	Lcd_cursor(&lcd, 0,3);
	Lcd_string(&lcd, "Frequency");
	/* USER CODE END 2 */

	/* Infinite loop */
	/* USER CODE BEGIN WHILE */
	while (1)
	{
		/* USER CODE END WHILE */

		/* USER CODE BEGIN 3 */
		while(idx < NS)
		{
			TIM1->CCR1 = sine_pwm1[idx];
			TIM1->CCR2 = sine_pwm2[idx];
			DELAY_US(delay_cont);
			idx++;
		}

		idx = 0;
		iters += 1;
		if(iters % 1000 == 0)
		{
			HAL_ADC_PollForConversion(&hadc1, 100);
			pot_value = HAL_ADC_GetValue(&hadc1);
			freq = (int)((pot_value*3000)/4095);
			delay_cont = (int)((10000 - freq)/freq);

			Lcd_clear(&lcd);
			Lcd_cursor(&lcd, 0,3);
			Lcd_string(&lcd, "Frequency");
			Lcd_cursor(&lcd, 1, 7);
			Lcd_int(&lcd, freq);
			iters = 0;
		}
	}
	/* USER CODE END 3 */
}

/**
  * @brief System Clock Configuration
  * @retval None
  */
void SystemClock_Config(void)
{
  RCC_OscInitTypeDef RCC_OscInitStruct = {0};
  RCC_ClkInitTypeDef RCC_ClkInitStruct = {0};
  RCC_PeriphCLKInitTypeDef PeriphClkInit = {0};

  /** Initializes the RCC Oscillators according to the specified parameters
  * in the RCC_OscInitTypeDef structure.
  */
  RCC_OscInitStruct.OscillatorType = RCC_OSCILLATORTYPE_HSI;
  RCC_OscInitStruct.HSIState = RCC_HSI_ON;
  RCC_OscInitStruct.HSICalibrationValue = RCC_HSICALIBRATION_DEFAULT;
  RCC_OscInitStruct.PLL.PLLState = RCC_PLL_ON;
  RCC_OscInitStruct.PLL.PLLSource = RCC_PLLSOURCE_HSI_DIV2;
  RCC_OscInitStruct.PLL.PLLMUL = RCC_PLL_MUL16;
  if (HAL_RCC_OscConfig(&RCC_OscInitStruct) != HAL_OK)
  {
    Error_Handler();
  }

  /** Initializes the CPU, AHB and APB buses clocks
  */
  RCC_ClkInitStruct.ClockType = RCC_CLOCKTYPE_HCLK|RCC_CLOCKTYPE_SYSCLK
                              |RCC_CLOCKTYPE_PCLK1|RCC_CLOCKTYPE_PCLK2;
  RCC_ClkInitStruct.SYSCLKSource = RCC_SYSCLKSOURCE_PLLCLK;
  RCC_ClkInitStruct.AHBCLKDivider = RCC_SYSCLK_DIV1;
  RCC_ClkInitStruct.APB1CLKDivider = RCC_HCLK_DIV2;
  RCC_ClkInitStruct.APB2CLKDivider = RCC_HCLK_DIV1;

  if (HAL_RCC_ClockConfig(&RCC_ClkInitStruct, FLASH_LATENCY_2) != HAL_OK)
  {
    Error_Handler();
  }
  PeriphClkInit.PeriphClockSelection = RCC_PERIPHCLK_ADC;
  PeriphClkInit.AdcClockSelection = RCC_ADCPCLK2_DIV8;
  if (HAL_RCCEx_PeriphCLKConfig(&PeriphClkInit) != HAL_OK)
  {
    Error_Handler();
  }
}

/**
  * @brief ADC1 Initialization Function
  * @param None
  * @retval None
  */
static void MX_ADC1_Init(void)
{

  /* USER CODE BEGIN ADC1_Init 0 */

  /* USER CODE END ADC1_Init 0 */

  ADC_ChannelConfTypeDef sConfig = {0};

  /* USER CODE BEGIN ADC1_Init 1 */

  /* USER CODE END ADC1_Init 1 */

  /** Common config
  */
  hadc1.Instance = ADC1;
  hadc1.Init.ScanConvMode = ADC_SCAN_DISABLE;
  hadc1.Init.ContinuousConvMode = ENABLE;
  hadc1.Init.DiscontinuousConvMode = DISABLE;
  hadc1.Init.ExternalTrigConv = ADC_SOFTWARE_START;
  hadc1.Init.DataAlign = ADC_DATAALIGN_RIGHT;
  hadc1.Init.NbrOfConversion = 1;
  if (HAL_ADC_Init(&hadc1) != HAL_OK)
  {
    Error_Handler();
  }

  /** Configure Regular Channel
  */
  sConfig.Channel = ADC_CHANNEL_6;
  sConfig.Rank = ADC_REGULAR_RANK_1;
  sConfig.SamplingTime = ADC_SAMPLETIME_1CYCLE_5;
  if (HAL_ADC_ConfigChannel(&hadc1, &sConfig) != HAL_OK)
  {
    Error_Handler();
  }
  /* USER CODE BEGIN ADC1_Init 2 */

  /* USER CODE END ADC1_Init 2 */

}

/**
  * @brief TIM1 Initialization Function
  * @param None
  * @retval None
  */
static void MX_TIM1_Init(void)
{

  /* USER CODE BEGIN TIM1_Init 0 */

  /* USER CODE END TIM1_Init 0 */

  TIM_MasterConfigTypeDef sMasterConfig = {0};
  TIM_OC_InitTypeDef sConfigOC = {0};
  TIM_BreakDeadTimeConfigTypeDef sBreakDeadTimeConfig = {0};

  /* USER CODE BEGIN TIM1_Init 1 */

  /* USER CODE END TIM1_Init 1 */
  htim1.Instance = TIM1;
  htim1.Init.Prescaler = 0;
  htim1.Init.CounterMode = TIM_COUNTERMODE_UP;
  htim1.Init.Period = 639;
  htim1.Init.ClockDivision = TIM_CLOCKDIVISION_DIV1;
  htim1.Init.RepetitionCounter = 0;
  htim1.Init.AutoReloadPreload = TIM_AUTORELOAD_PRELOAD_DISABLE;
  if (HAL_TIM_PWM_Init(&htim1) != HAL_OK)
  {
    Error_Handler();
  }
  sMasterConfig.MasterOutputTrigger = TIM_TRGO_RESET;
  sMasterConfig.MasterSlaveMode = TIM_MASTERSLAVEMODE_DISABLE;
  if (HAL_TIMEx_MasterConfigSynchronization(&htim1, &sMasterConfig) != HAL_OK)
  {
    Error_Handler();
  }
  sConfigOC.OCMode = TIM_OCMODE_PWM1;
  sConfigOC.Pulse = 0;
  sConfigOC.OCPolarity = TIM_OCPOLARITY_HIGH;
  sConfigOC.OCNPolarity = TIM_OCNPOLARITY_HIGH;
  sConfigOC.OCFastMode = TIM_OCFAST_DISABLE;
  sConfigOC.OCIdleState = TIM_OCIDLESTATE_RESET;
  sConfigOC.OCNIdleState = TIM_OCNIDLESTATE_RESET;
  if (HAL_TIM_PWM_ConfigChannel(&htim1, &sConfigOC, TIM_CHANNEL_1) != HAL_OK)
  {
    Error_Handler();
  }
  if (HAL_TIM_PWM_ConfigChannel(&htim1, &sConfigOC, TIM_CHANNEL_2) != HAL_OK)
  {
    Error_Handler();
  }
  sBreakDeadTimeConfig.OffStateRunMode = TIM_OSSR_DISABLE;
  sBreakDeadTimeConfig.OffStateIDLEMode = TIM_OSSI_DISABLE;
  sBreakDeadTimeConfig.LockLevel = TIM_LOCKLEVEL_OFF;
  sBreakDeadTimeConfig.DeadTime = 8;
  sBreakDeadTimeConfig.BreakState = TIM_BREAK_DISABLE;
  sBreakDeadTimeConfig.BreakPolarity = TIM_BREAKPOLARITY_HIGH;
  sBreakDeadTimeConfig.AutomaticOutput = TIM_AUTOMATICOUTPUT_DISABLE;
  if (HAL_TIMEx_ConfigBreakDeadTime(&htim1, &sBreakDeadTimeConfig) != HAL_OK)
  {
    Error_Handler();
  }
  /* USER CODE BEGIN TIM1_Init 2 */

  /* USER CODE END TIM1_Init 2 */
  HAL_TIM_MspPostInit(&htim1);

}

/**
  * @brief GPIO Initialization Function
  * @param None
  * @retval None
  */
static void MX_GPIO_Init(void)
{
  GPIO_InitTypeDef GPIO_InitStruct = {0};
/* USER CODE BEGIN MX_GPIO_Init_1 */
/* USER CODE END MX_GPIO_Init_1 */

  /* GPIO Ports Clock Enable */
  __HAL_RCC_GPIOD_CLK_ENABLE();
  __HAL_RCC_GPIOA_CLK_ENABLE();
  __HAL_RCC_GPIOB_CLK_ENABLE();

  /*Configure GPIO pin Output Level */
  HAL_GPIO_WritePin(GPIOA, GPIO_PIN_0|GPIO_PIN_1|GPIO_PIN_2|GPIO_PIN_3
                          |GPIO_PIN_4|GPIO_PIN_5, GPIO_PIN_RESET);

  /*Configure GPIO pins : PA0 PA1 PA2 PA3
                           PA4 PA5 */
  GPIO_InitStruct.Pin = GPIO_PIN_0|GPIO_PIN_1|GPIO_PIN_2|GPIO_PIN_3
                          |GPIO_PIN_4|GPIO_PIN_5;
  GPIO_InitStruct.Mode = GPIO_MODE_OUTPUT_PP;
  GPIO_InitStruct.Pull = GPIO_NOPULL;
  GPIO_InitStruct.Speed = GPIO_SPEED_FREQ_LOW;
  HAL_GPIO_Init(GPIOA, &GPIO_InitStruct);

/* USER CODE BEGIN MX_GPIO_Init_2 */
/* USER CODE END MX_GPIO_Init_2 */
}

/* USER CODE BEGIN 4 */

/* USER CODE END 4 */

/**
  * @brief  This function is executed in case of error occurrence.
  * @retval None
  */
void Error_Handler(void)
{
  /* USER CODE BEGIN Error_Handler_Debug */
  /* User can add his own implementation to report the HAL error return state */
  __disable_irq();
  while (1)
  {
  }
  /* USER CODE END Error_Handler_Debug */
}

#ifdef  USE_FULL_ASSERT
/**
  * @brief  Reports the name of the source file and the source line number
  *         where the assert_param error has occurred.
  * @param  file: pointer to the source file name
  * @param  line: assert_param error line source number
  * @retval None
  */
void assert_failed(uint8_t *file, uint32_t line)
{
  /* USER CODE BEGIN 6 */
  /* User can add his own implementation to report the file name and line number,
     ex: printf("Wrong parameters value: file %s on line %d\r\n", file, line) */
  /* USER CODE END 6 */
}
#endif /* USE_FULL_ASSERT */
